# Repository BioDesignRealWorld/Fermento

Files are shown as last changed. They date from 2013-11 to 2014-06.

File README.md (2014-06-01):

Fermento
========

An open-source incubator for fun and profit. For more information about the project, see [biodesign.cc](http://biodesign.cc/2013/12/25/diy-incubator/).

Board
-----

* __Fab__ contains the PCB version to send to a professional PCB fabrication house. It has a nice silkscreen and slightly better component layout. 
* __Homebrew__ contains the version for homebrew PCB printing. The layout is one-sided for easier manufacturing. Drill plan and assembly instruction sheet included.
  To accomodate a single sided board, the wiring of the component to the microcontroller had to be changed. The correct pin mapping can be changed by a single line
  in the firmware.

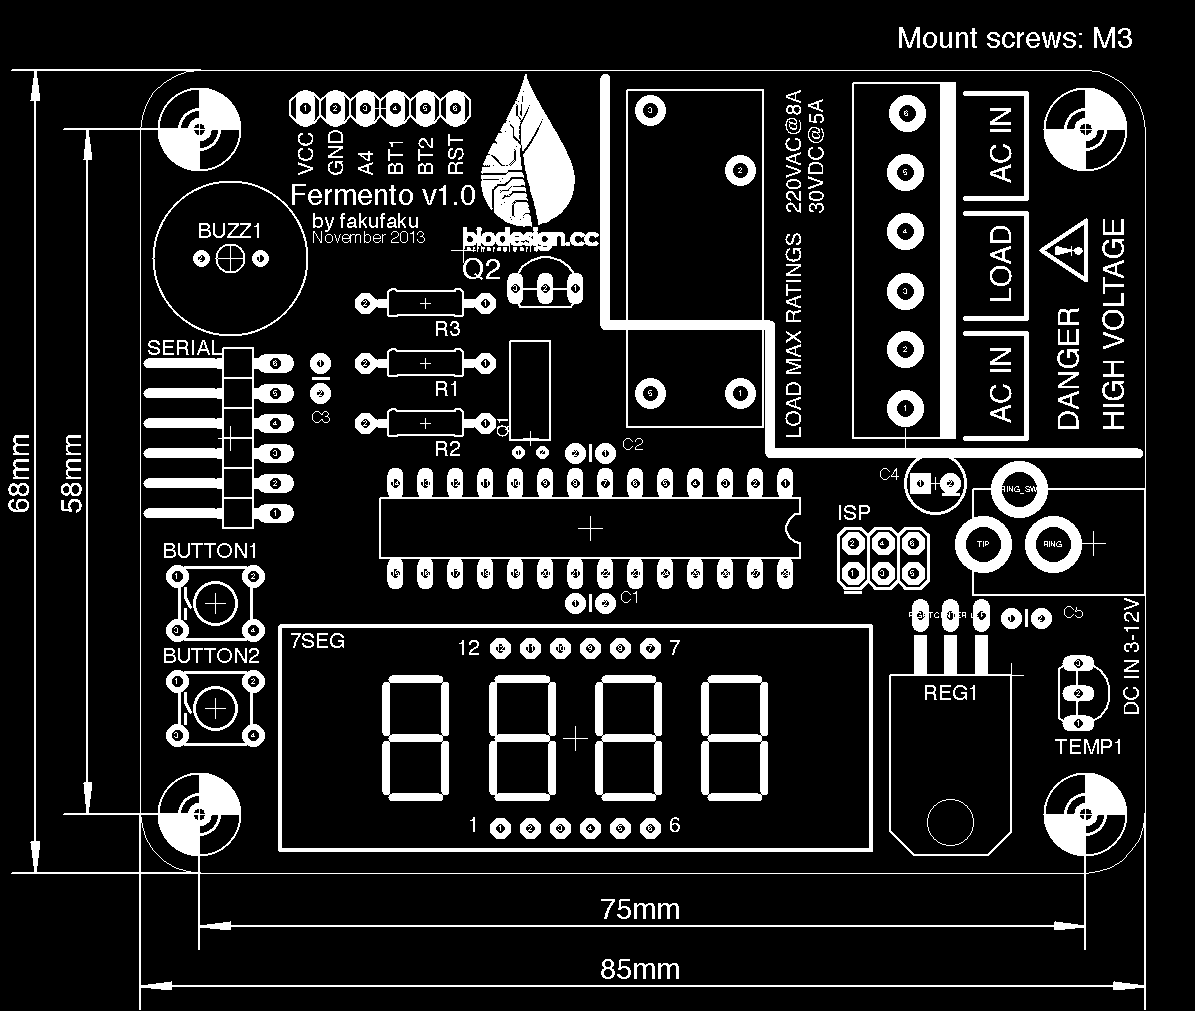
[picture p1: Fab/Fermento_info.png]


Bill Of Material
----------------

* 1x ATmega328p
* 1x DIP28 socket 
* 2x Tactile switch (through hole) (BUTTON1, BUTTON2) (C&K PTS645SM95-2 LFS)
* 2x Resistor 10K (R1, R3)
* 1x Resistor 1K (R2)
* 4x Capacitor 0.1uF, 2.5 mm pin spacing (C1, C2, C3, C5)
* 1x Electrolytic capacitor 47uF, radial, 2.5 mm pin spacing (C4)
* 1x 6-pin 90-degrees header (SERIAL)
* 1x 3x2-pin straight header (ISP)
* 1x 6-terminal screw block (Altech MBE-156)
* 1x Relay, 3VDC switching (Omron G6RL-1A-DC3)
* 1x 13mm buzzer (BUZZ1) (Murata, PKM13EPYH4000-A0)
* 1x DC jack 2.1mm (Kobiconn 163-179PH-EX)
* 1x 32.768kHz crystal (Q1) (ECS-.327-12.5-13X)
* 1x Mosfet transistor, TO92 (Q2) (Supertex TP2104N3-G)
* 1x 3.3V Regulator, TO220 (REG1) (TI TLV2217-33KCSE3)
* 1x Temperature sensor, TO92 (TEMP1) (TI LM61CIZ/NOPB)
* 1x 7-segment 4-digit display (7SEG) (Lumex LDQ-N514RI)

Wiring of the incubator
-----------------------

The board has a 6 pin terminal that allows minimal effort in wiring all the AC part of the circuit.

* The 2 wires from the bulb socket go into __LOAD__.
* The 2 wires from the plug go into one of the __AC IN__ terminal.
* The second __AC IN__ can be used to attach a female AC socket. This allows to connect there a DC outlet to power the board.

Power supply
------------

The board has a 2.1mm DC jack. The DC regulator requires an input of 3-12V DC.

Firmware
--------

To install the firmware in your Arduino IDE, do the following.

* Copy the folder `firmware/Fermento` to your local Arduino folder.
* Copy the content of `firmware/hardware` to local `Arduino/hardware`.
* Copy the content of `firmware/libraries` to local `Arduino/libraries`.

Then, chose `Tools -> Board -> ATmega328p on a breadboard`. Choose the sketch
`Fermento` from the sketchbook, and upload it.

In case you don't use the homebrew version, there is one line to comment out in
the sketch to change the pin mapping.

In the Fab version, an ISP header is provided to burn the bootloader. The Homebrew
version is lacking this, so a different board (such as the standard Arduino) needs
to be used to burn the bootloader. In addition, an ISP-programmer is needed.
An Arduino board can also be used to do [the job](http://arduino.cc/en/Tutorial/ArduinoISP).

Use it
------

Button1 and button2 control the incubation temperature and time respectively.

When button1 is shortly pressed the display switches to temperature. To set the
incubation temperature, keep button1 pressed until it displays the desired
temperature. The temperature regulation starts as soon as an incubation
temperatures different than 0 is set. Note that if the incubation temperature
is lower than room temperature, nothing happens.

When button2 is shortly pressed the display switches to incubation time
(hours:minutes). To set the incubation time, keep button2 pressed until the
desired incubation time is displayed. If you don’t set an incubation time, the
incubation will never stop. The time goes up in increments of 30 minutes.

Pressing button1 and button2 together for a few seconds resets incubation temperature and time to 0.

License
-------

2013 (c) Robin Scheibler, [CC BY-SA 3.0](https://creativecommons.org/licenses/by-sa/3.0/).

Based on [TokyoTime](http://robinscheibler.org/TokyoTime), itself based on SparkFun's [BigTime](https://www.sparkfun.com/products/11734).

The code uses the [Arduino PID library](http://playground.arduino.cc/Code/PIDLibrary).

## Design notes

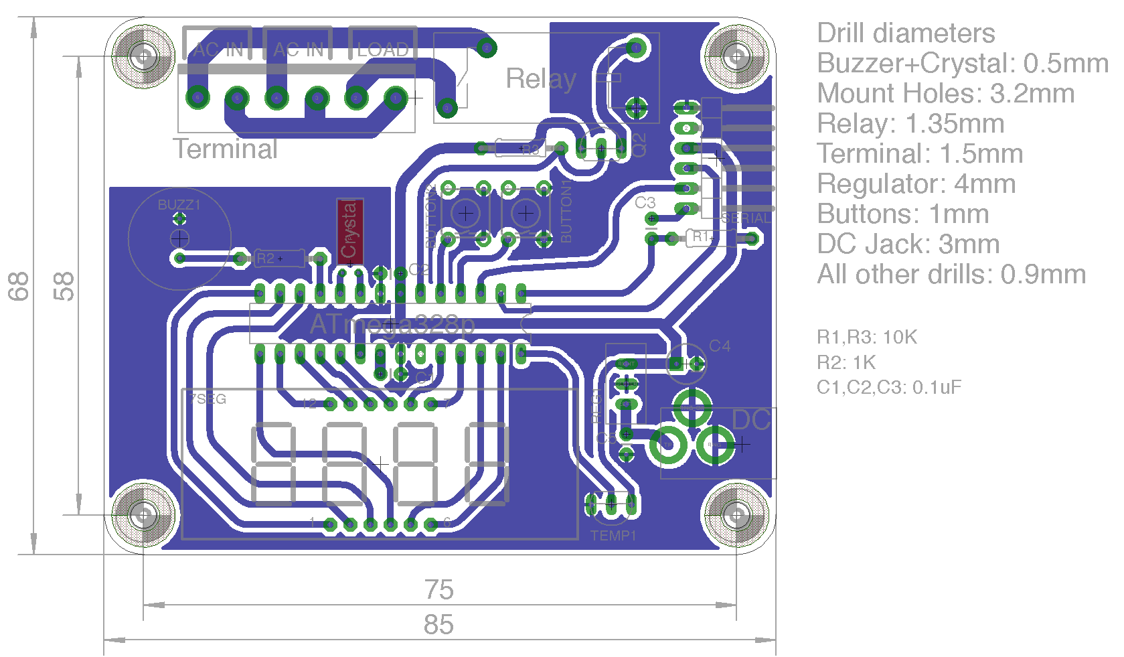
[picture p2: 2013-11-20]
Homebrew/Fermento_1side_brd.png

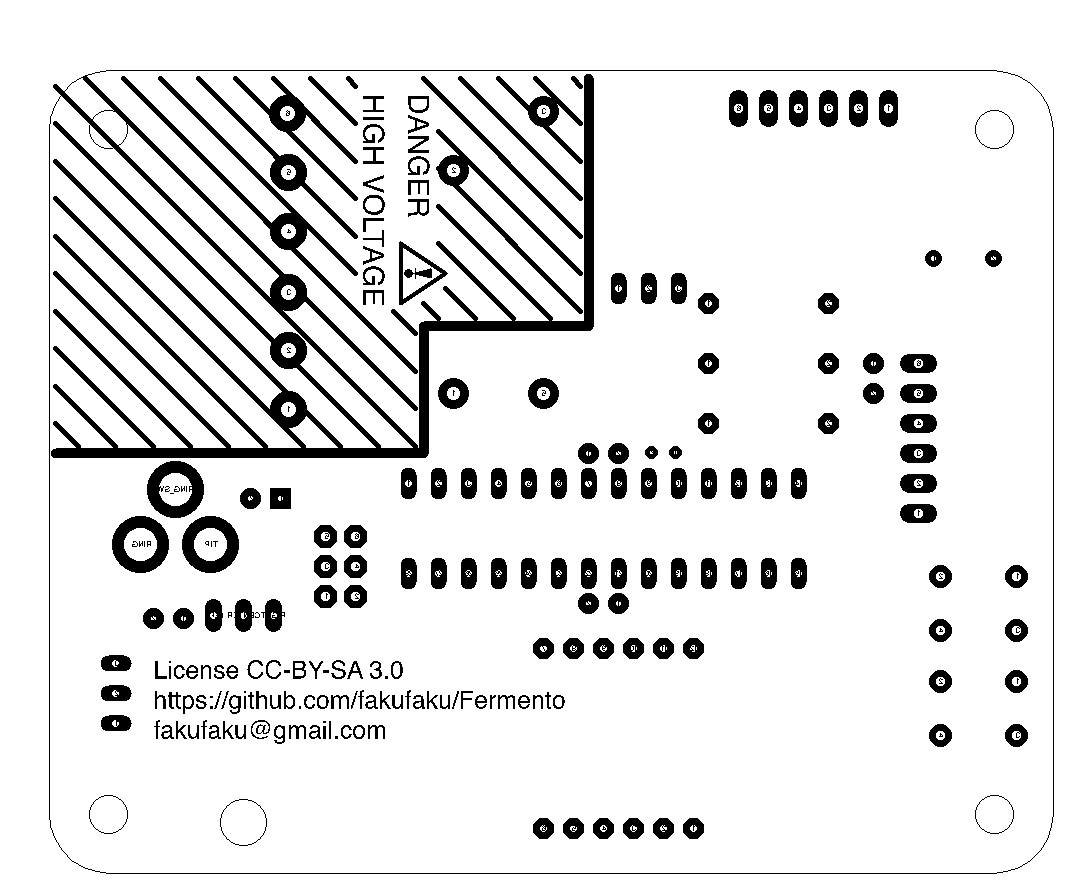
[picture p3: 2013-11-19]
Fab/Fermento_bot.png

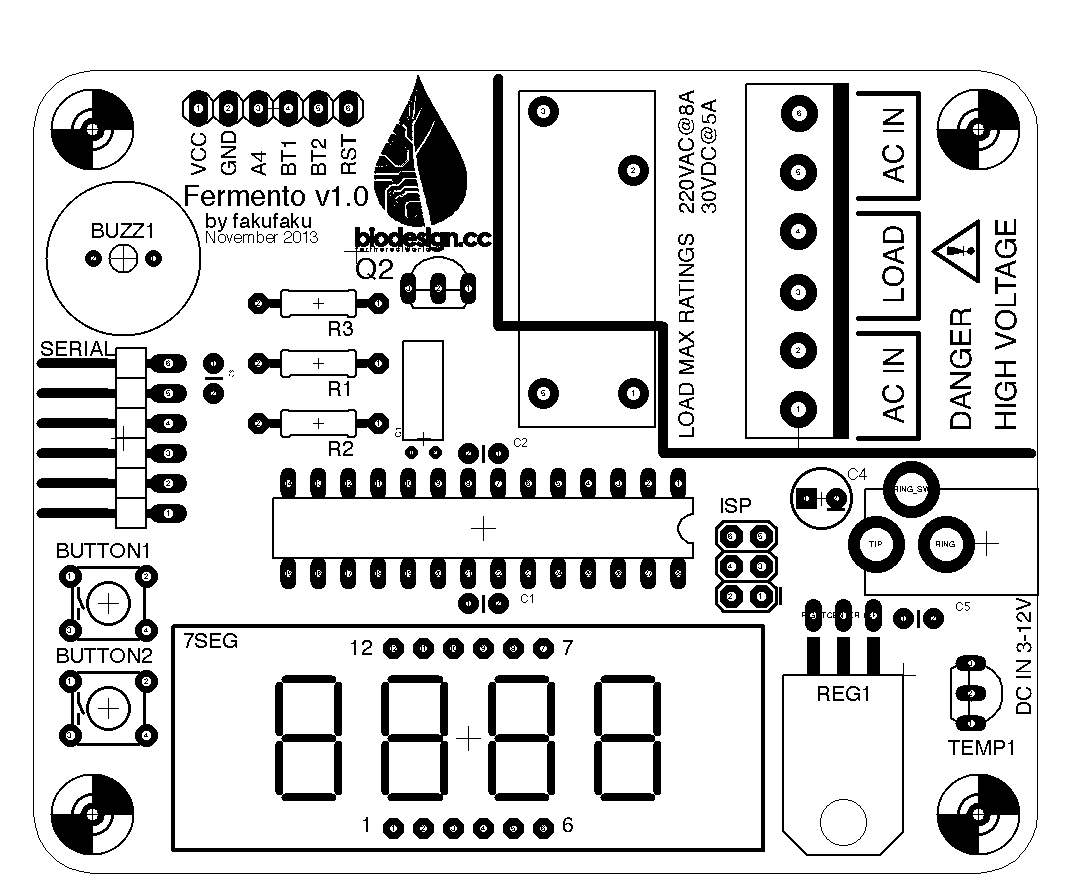
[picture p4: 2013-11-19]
Fab/Fermento_top.png

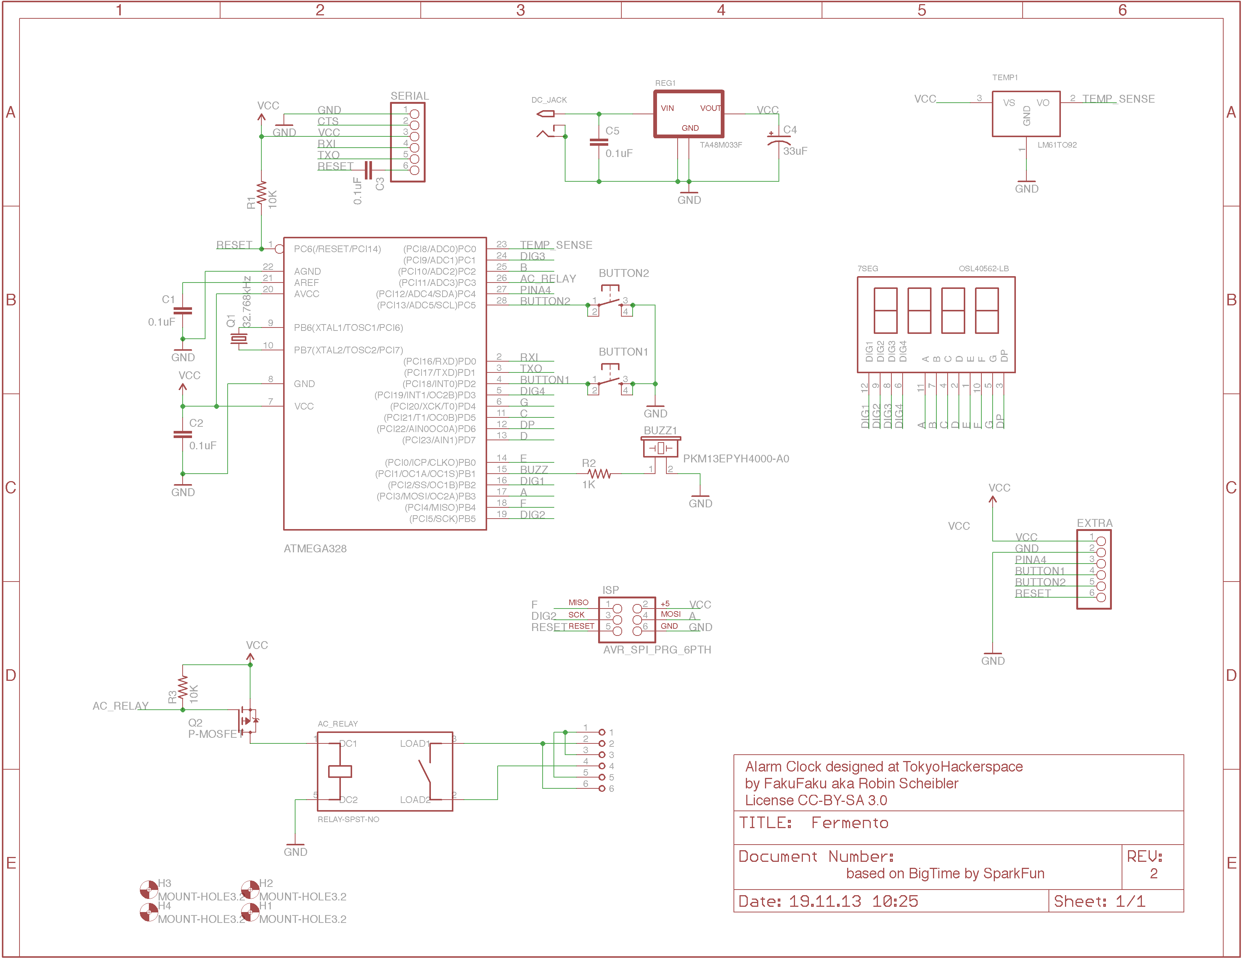
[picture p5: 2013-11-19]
Fab/Fermento_sch.png

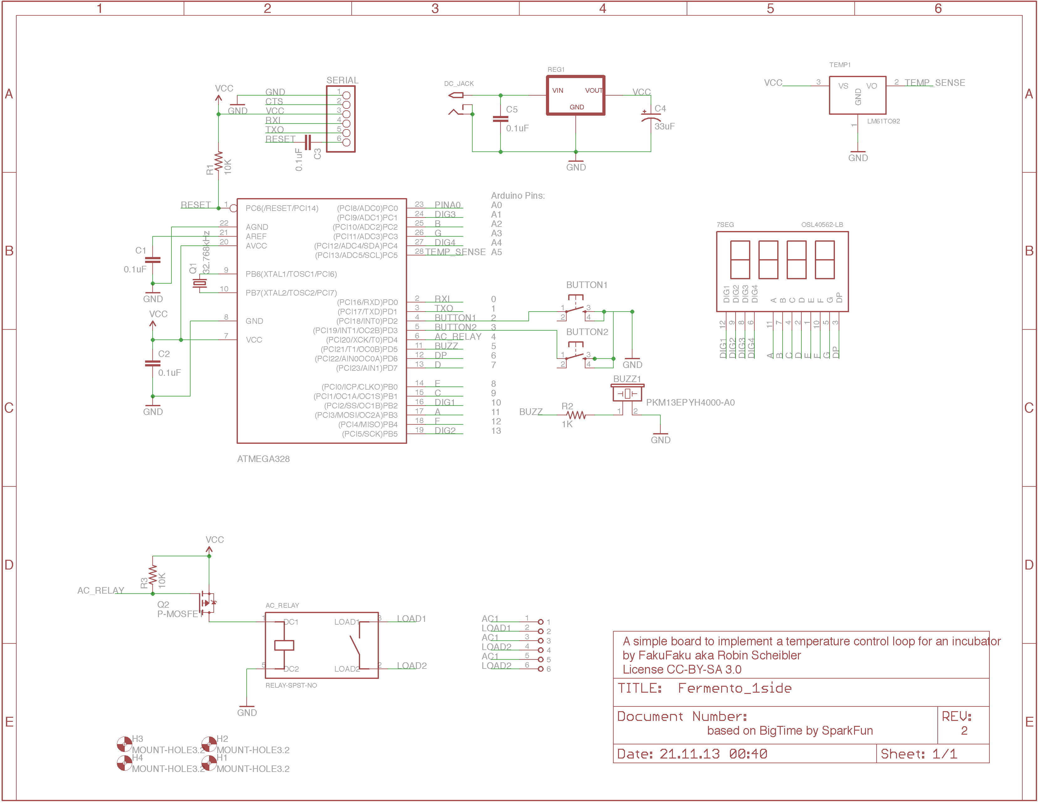
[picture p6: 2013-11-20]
Homebrew/Fermento_1side_sch.png

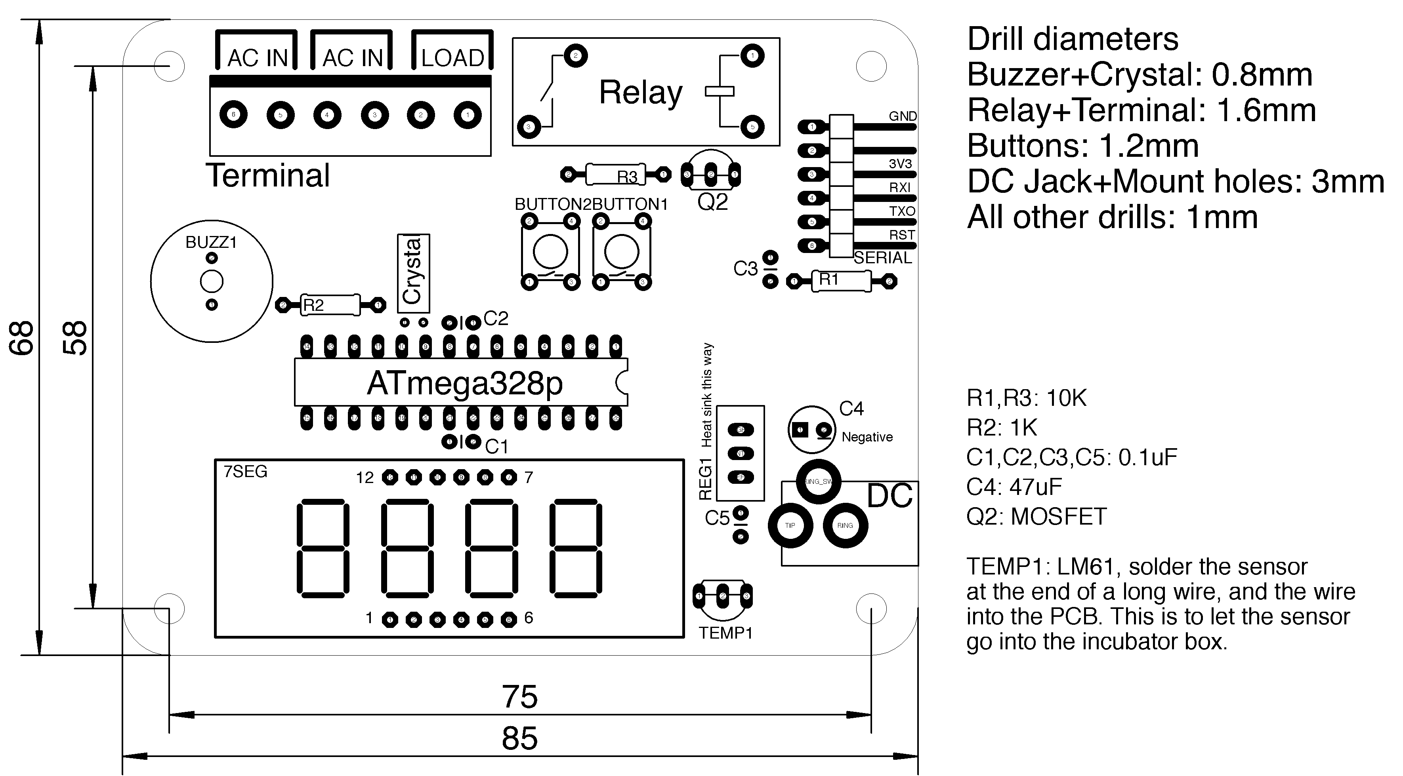
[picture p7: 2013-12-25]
Homebrew/Fermento_1side_info.png

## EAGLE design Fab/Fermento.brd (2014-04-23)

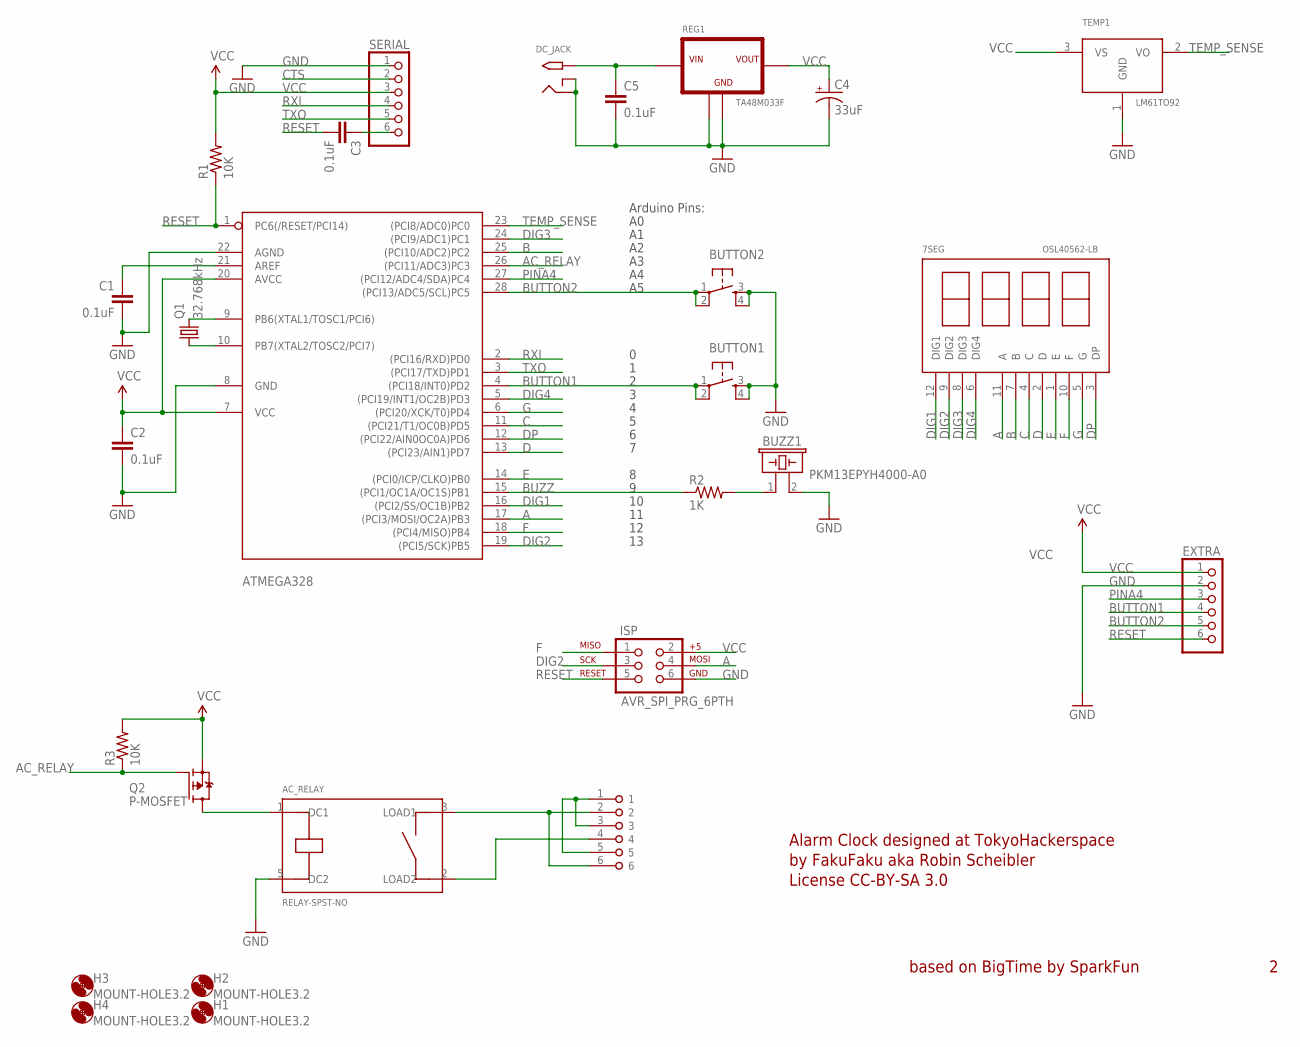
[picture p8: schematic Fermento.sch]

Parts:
7SEG: OSL40562-LB; OSL40562
AC_RELAY: RELAY-SPST-NO; G6RL-1A-DC3
ATMEGA328: ATMEGA168-20P; DIL28-3
BUTTON1, BUTTON2: TAC_SWITCHPTH; TACTILE-PTH
BUZZ1: PKM13EPYH4000-A0; PIEZO-MURATA-13MM
C1, C2, C3, C5: 0.1uF; CAP-PTH-SMALL
C4: 33uF; CPOL-RADIAL-10UF-25V
DC_JACK: 2.1MMJACKTHM; PJ-102A
EXTRA: PINHD-1X6; 1X06
H1, H2, H3, H4: MOUNT-HOLE3.2; 3,2
ISP: AVR_SPI_PRG_6PTH; 2X3
Q1: 32.768kHz; CRYSTAL-8X3-TH
Q2: P-MOSFET; TO92-
R1, R3: 10K; 0207/10
R2: 1K; 0207/10
REG1: TA48M033F; TO-220
SERIAL: PINHD-1X6/90; 1X06/90
TEMP1: LM61TO92; TO92-
U$2: TERMINAL-6; MBE-156

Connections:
A: 7SEG.11 (A), ATMEGA328.17 ((PCI3/MOSI/OC2A)PB3), ISP.4
AC_RELAY: ATMEGA328.26 ((PCI11/ADC3)PC3), Q2.2 (G), R3.1
AREF: ATMEGA328.21 (AREF), C1.1
B: 7SEG.7 (B), ATMEGA328.25 ((PCI10/ADC2)PC2)
BUTTON1: ATMEGA328.4 ((PCI18/INT0)PD2), BUTTON1.1, BUTTON1.2, EXTRA.4
BUTTON2: ATMEGA328.28 ((PCI13/ADC5/SCL)PC5), BUTTON2.1, BUTTON2.2, EXTRA.5
BUZZ: ATMEGA328.15 ((PCI1/OC1A/OC1S)PB1), R2.1
C: 7SEG.4 (C), ATMEGA328.11 ((PCI21/T1/OC0B)PD5)
CTS: SERIAL.2
D: 7SEG.2 (D), ATMEGA328.13 ((PCI23/AIN1)PD7)
DIG1: 7SEG.12 (DIG1), ATMEGA328.16 ((PCI2/SS/OC1B)PB2)
DIG2: 7SEG.9 (DIG2), ATMEGA328.19 ((PCI5/SCK)PB5), ISP.3
DIG3: 7SEG.8 (DIG3), ATMEGA328.24 ((PCI9/ADC1)PC1)
DIG4: 7SEG.6 (DIG4), ATMEGA328.5 ((PCI19/INT1/OC2B)PD3)
DP: 7SEG.3 (DP), ATMEGA328.12 ((PCI22/AIN0OC0A)PD6)
E: 7SEG.1 (E), ATMEGA328.14 ((PCI0/ICP/CLKO)PB0)
F: 7SEG.10 (F), ATMEGA328.18 ((PCI4/MISO)PB4), ISP.1
G: 7SEG.5 (G), ATMEGA328.6 ((PCI20/XCK/T0)PD4)
GND: AC_RELAY.5 (DC2), ATMEGA328.8 (GND), ATMEGA328.22 (AGND), BUTTON1.3, BUTTON1.4, BUTTON2.3, BUTTON2.4, BUZZ1.2, C1.2, C2.2, C4.2 (-), C5.2, DC_JACK.RING, DC_JACK.RING_SW, EXTRA.2, ISP.6, REG1.CENTER (GND), REG1.THERMAL (GND), SERIAL.1, TEMP1.1 (GND)
unnamed: ATMEGA328.9 (PB6(XTAL1/TOSC1/PCI6)), Q1.2
unnamed: ATMEGA328.10 (PB7(XTAL2/TOSC2/PCI7)), Q1.1
unnamed: C5.1, DC_JACK.TIP, REG1.LEFT (VIN)
unnamed: U$2.1, U$2.3, U$2.5
unnamed: AC_RELAY.3 (LOAD1), U$2.2, U$2.6
unnamed: C3.1, SERIAL.6
unnamed: AC_RELAY.2 (LOAD2), U$2.4
unnamed: BUZZ1.1, R2.2
PINA4: ATMEGA328.27 ((PCI12/ADC4/SDA)PC4), EXTRA.3
RELAY: AC_RELAY.1 (DC1), Q2.1 (D)
RESET: ATMEGA328.1 (PC6(/RESET/PCI14)), C3.2, EXTRA.6, ISP.5, R1.1
RXI: ATMEGA328.2 ((PCI16/RXD)PD0), SERIAL.4
TEMP_SENSE: ATMEGA328.23 ((PCI8/ADC0)PC0), TEMP1.2 (VO)
TXO: ATMEGA328.3 ((PCI17/TXD)PD1), SERIAL.5
VCC: ATMEGA328.7 (VCC), ATMEGA328.20 (AVCC), C2.1, C4.1 (+), EXTRA.1, ISP.2, Q2.3 (S), R1.2, R3.2, REG1.RIGHT (VOUT), SERIAL.3, TEMP1.3 (VS)

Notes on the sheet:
Alarm Clock designed at TokyoHackerspace
by FakuFaku aka Robin Scheibler
License CC-BY-SA 3.0
based on BigTime by SparkFun
Arduino Pins:

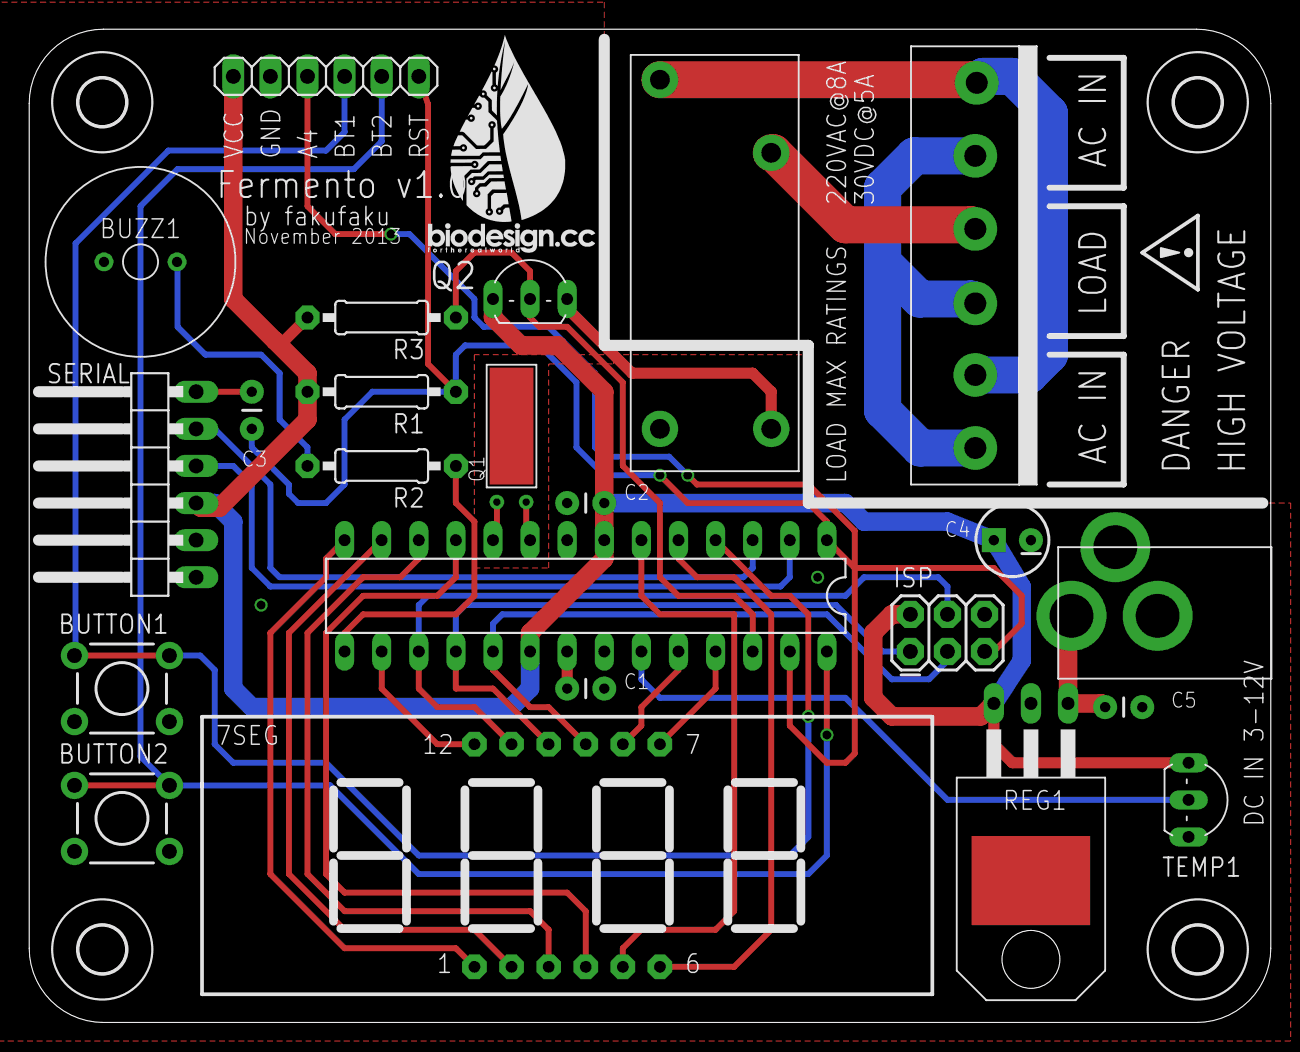
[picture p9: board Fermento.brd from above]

Board: 2 copper layers, 85.0 x 68.0 mm, 30 parts (1 on the bottom side), 33 nets.

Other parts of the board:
U$1, U$3: DANGER-SMALL
U$4: BIODESIGN-LOGO

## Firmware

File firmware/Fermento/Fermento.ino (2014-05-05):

/*
 * (c) Fakufaku 2013
 * This is the code for the homebrew incubator 'Fermento'
 * This code is released under the CC-BY-SA 3.0 License.
 * The part of the code that's used for the display on the 7-segment was ripped off the BigTime code from Nathan Seidl. I owe him a beer then.
 */

#include <math.h>

#include <PID_v1.h>

#define TRUE 1
#define FALSE 0

#define ENTER_CRIT()    {byte volatile saved_sreg = SREG; cli()
#define LEAVE_CRIT()    SREG = saved_sreg;}

//Careful messing with the system color, you can damage the display if
//you assign the wrong color. If you're in doubt, set it to red and load the code,
//then see what the color is.
#define RED  1
#define GREEN 2
#define BLUE  3
#define YELLOW  4
int systemColor = RED;
int display_brightness = 2000; //A larger number makes the display more dim. This is set correctly below.

// These define control how to turn on digits and segments
// Change these according to the type of seven-segment used (common anode/cathode)
// The default is set for common cathode
#define DIGIT_ON   LOW
#define DIGIT_OFF  HIGH
#define SEGMENT_ON  HIGH
#define SEGMENT_OFF LOW

// slow continuous PWM variables
#define PWM_MS 5000
#define PWM_MIN 100
#define RELAY_ON  LOW
#define RELAY_OFF HIGH

// PID loop parameter
#define PID_KP  50
#define PID_KI  1
#define PID_KD  1

// Some display related parameters (time in seconds, temperature in degrees Celsius)
#define TIME_INCREMENT 1800
#define MAX_TIME 356459
#define TEMP_INCREMENT 1
#define MAX_TEMP 65

//-=-=-=-=-=-=-=-=-=-=-=-=-=-=-=-=-=-=
// OPTIONS
//
// Voltage reference of the ADC
#define ADC_REF 3300
//
// Uncomment following line for the homebrew (1-sided) PCB version
//#define FERMENTO_1SIDE
//
// Uncomment the following line if you use the LM35 instead of the LM61 temperature sensor
//#define LM35
//-=-=-=-=-=-=-=-=-=-=-=-=-=-=-=-=-=-=

//-=-=-=-=-=-=-=-=-=-=-=-=-=-=-=-=-=-=
//Pin definitions
#ifdef FERMENTO_1SIDE
int digit1 = 10;    //Display pin 12
int digit2 = 13;    //Display pin 9
int digit3 = A1;    //Display pin 8
int digit4 = A4;     //Display pin 6

int segA = 11;      //Display pin 11
int segB = A2;      //Display pin 7
int segC = 9;       //Display pin 4
int segD = 7;       //Display pin 2
int segE = 8;       //Display pin 1
int segF = 12;      //Display pin 10
int segG = A3;       //Display pin 5

int colons = 6;     //Display pin 3

int temp_sen = A5;  // to read the temperature sensor

const static int buzz = 5;
const static int theButton = 2;
const static int theButton2 = 3;
const static int pwm_pin = 4;  // Pin 4

// The interrupt of button1 is on external interrupt 0
// The interrupt of button2 is on external interrupt 1
#define BUTTON1_INT_VECT INT0_vect
#define BUTTON2_INT_VECT INT1_vect
#define BUTTONS_INT_SET() do  \
  {                           \
    EICRA = (1<<ISC11) + (1<<ISC01); /* falling edge */ \
    EIMSK = (1<<INT1) + (1<<INT0);      \
  }                           \
  while (0)

#else

// Pin definition for the 2-layer PCB
int digit1 = 10;    //Display pin 12
int digit2 = 13;    //Display pin 9
int digit3 = A1;    //Display pin 8
int digit4 = 3;     //Display pin 6

int segA = 11;      //Display pin 11
int segB = A2;      //Display pin 7
int segC = 5;       //Display pin 4
int segD = 7;       //Display pin 2
int segE = 8;       //Display pin 1
int segF = 12;      //Display pin 10
int segG = 4;       //Display pin 5

int colons = 6;     //Display pin 3

int temp_sen = A0;  // to read the temperature sensor

const static int buzz = 9;
const static int theButton = 2;
const static int theButton2 = A5;
const static int pwm_pin = A3;  // Pin 4

// The interrupt of button1 is on external interrupt 0
// The interrupt of button2 is on PCINT13 (A5), on PCIE1.
#define BUTTON1_INT_VECT INT0_vect
#define BUTTON2_INT_VECT PCINT1_vect
#define BUTTONS_INT_SET() do  \
  {                           \
    EICRA = (1<<ISC01); /* falling edge */     \
    EIMSK = (1<<INT0);        \
    PCICR = (1 << PCIE1);     \
    PCMSK1 = (1 << PCINT13);  \
  }                           \
  while (0)

#endif
//-=-=-=-=-=-=-=-=-=-=-=-=-=-=-=-=-=-=


// Display status variable
#define TIME 1
#define TEMP 2
int display_status = TEMP;
int backoff = 0;  // just a short backoff for when we switch the display between TIME/TEMP
#define BACKOFFTIME 2
char disp_str[4];

// Variable to keep track of PWM window
unsigned long windowStartTime;

// control variables for PID
double t_incub;      // input to PID (temperature in incubator)
double t_incub_N;    // number of samples in t_incub average
double pwm_duty;     // output of PID
double t_set = 0;    // set point (target temperature)

//Specify the links and initial tuning parameters
PID myPID(&t_incub, &pwm_duty, &t_set, PID_KP, PID_KI, PID_KD, DIRECT);

// display timer (freeze parameters to display for 2 seconds)
int t_incub_disp;

// Timer variables
unsigned long timer_seconds = 0;

//The very important 32.686kHz interrupt handler
SIGNAL(TIMER2_OVF_vect)
{

  ENTER_CRIT();

  if (timer_seconds > 1)
  {
    timer_seconds--;
  }
  else if (timer_seconds == 1)
  {
    // reset timer
    timer_seconds = 0;
    // turn off by setting target temperature to zero
    t_set = 0;
    // Reset the PID
    myPID.SetMode(MANUAL);
    myPID.SetMode(AUTOMATIC);
  }

  // decrement backoff
  if (backoff > 0)
    backoff--;

  LEAVE_CRIT();
}

//The interrupt occurs when you push the button
SIGNAL(BUTTON1_INT_VECT)
{
  ENTER_CRIT();
  display_status = TEMP;
  backoff = BACKOFFTIME;
  LEAVE_CRIT();
}

SIGNAL(BUTTON2_INT_VECT)
{
  ENTER_CRIT();
  display_status = TIME;
  backoff = BACKOFFTIME;
  LEAVE_CRIT();
}

void setup()
{
  Serial.begin(57600);

  // set ADC reference to 3.3V
  analogReference(DEFAULT);

  // initialize pwm drive pin, and turn it off
  pinMode(pwm_pin, OUTPUT);
  digitalWrite(pwm_pin, HIGH);

  // initialize buzzer pin
  pinMode(buzz, OUTPUT);

  // initialize the buttons
  pinMode(theButton, INPUT);
  digitalWrite(theButton, HIGH); // pull-up
  pinMode(theButton2, INPUT);
  digitalWrite(theButton2, HIGH); // pull-up
  BUTTONS_INT_SET();

  //Setup TIMER2
  TCCR2A = 0x00;
  TCCR2B = (1<<CS22)|(1<<CS20); //Set CLK/128 or overflow interrupt every 1s
  ASSR   = (1<<AS2); //Enable asynchronous operation
  TIMSK2 = (1<<TOIE2); //Enable the timer 2 interrupt

  //These pins are used to control the display
  pinMode(segA, OUTPUT);
  pinMode(segB, OUTPUT);
  pinMode(segC, OUTPUT);
  pinMode(segD, OUTPUT);
  pinMode(segE, OUTPUT);
  pinMode(segF, OUTPUT);
  pinMode(segG, OUTPUT);

  pinMode(digit1, OUTPUT);
  pinMode(digit2, OUTPUT);
  pinMode(digit3, OUTPUT);
  pinMode(digit4, OUTPUT);
  pinMode(colons, OUTPUT);

  // setup PID stuff
  myPID.SetOutputLimits(PWM_MIN-1, PWM_MS-PWM_MIN+1);
  myPID.SetMode(AUTOMATIC);
  myPID.SetSampleTime(PWM_MS);
  windowStartTime = millis();

  // initialize pwm
  pwm_duty = 0; // off
  t_incub = read_temperature();
  t_incub_N = 1;

  // initialize slow variables for display
  t_incub_disp = t_incub;

}

void loop()
{
  
  temperatureControl();

  // display and output to serial
  if (display_status == TEMP)
  {
    displayTemperature((int)(t_incub_disp), FALSE); //Each call takes about 8ms, display the colon
  }
  else
  {
    unsigned int timer_disp;
    if (timer_seconds % 60 != 0)
      timer_disp = seconds2hours_minutes(timer_seconds + (60 - (timer_seconds%60)));
    else
      timer_disp = seconds2hours_minutes(timer_seconds);
    displayTime(timer_disp, TRUE); //Each call takes about 8ms, display the colon 
  }

  // handle buttons
  int b1 = digitalRead(theButton);
  int b2 = digitalRead(theButton2);

  if (b1 == LOW && b2 == LOW)
  {
    delay(10);
    if (backoff == 0)
    {
      // system reset
      timer_seconds = 0;
      t_set = 0;
      // reset PID
      myPID.SetMode(MANUAL);
      myPID.SetMode(AUTOMATIC);
    }
  }
  else if (b1 == LOW)
  {
    delay(10);
    if (backoff == 0)
      setTemperature();
  }
  else if (b2 == LOW)
  {
    delay(10);
    if (backoff == 0)
      setTime();
  }

}

// Simple PWM based on millis directly
void temperatureControl()
{
  unsigned long now = millis();

  // averaging over the whole 5 seconds
  t_incub += (read_temperature() - t_incub)/(++t_incub_N);

  if(now - windowStartTime > PWM_MS)
  { 
    // compute new pwm value for that window
    if (t_set != 0)
      myPID.Compute();

    // start a new relay window
    windowStartTime = now;

    // restart averaging of temperature
    t_incub_disp = t_incub;
    t_incub = read_temperature();
    t_incub_N = 1;

  }

  // if t_set is zero, that means incubator is off
  if (t_set < 1)
  {
    pwm_duty = 0;
  }

  // control the slow PWM
  if (pwm_duty < PWM_MIN)
  {
    digitalWrite(pwm_pin, RELAY_OFF);
  }
  else if (pwm_duty < PWM_MS-PWM_MIN)
  {
    if(pwm_duty > now - windowStartTime) 
      digitalWrite(pwm_pin, RELAY_ON);
    else 
      digitalWrite(pwm_pin, RELAY_OFF);
  }
  else
  {
    digitalWrite(pwm_pin, RELAY_ON);
  }
}

float read_temperature()
{
  // make an average of 10 readings of the ADC
  float A = 0;
  for (int i=0 ; i < 10 ; i++)
    A += analogRead(temp_sen);
  A /= 10;

  // convert the ADC output to a temperature
#ifndef LM35
  // LM61 sensor
  return (A/1023.*ADC_REF - 600)/10;
#else
  // LM35 sensor
  return (A/1023.*ADC_REF)/10;
#endif
}

//This routine occurs when you hold the button 1 down
//The colon blinks indicating we are in this mode
//Holding the button down will increase the time (accelerates)
//Releasing the button for more than 2 seconds will exit this mode
void setTemperature()
{
  ENTER_CRIT();

  int idleMiliseconds = 0;
  //This is the timeout counter. Once we get to ~2 seconds of inactivity, the watch
  //will exit the setTemperature function and return to normal operation

  while(idleMiliseconds < 2000) {

    for(int x = 0 ; x < 10 ; x++) {
      displayTemperature(t_set, TRUE); //Each call takes about 8ms, display the colon for about 100ms
      delayMicroseconds(display_brightness); //Wait before we paint the display again
    }
    for(int x = 0 ; x < 10 ; x++) {
      displayTemperature(t_set, FALSE); //Each call takes about 8ms, turn off the colon for about 100ms
      delayMicroseconds(display_brightness); //Wait before we paint the display again
    }

    //If you're still hitting the button, then increase the time and reset the idleMili timeout variable
    if(digitalRead(theButton) == LOW) {
      idleMiliseconds = 0;

      t_set = ((int)(t_set+TEMP_INCREMENT) % MAX_TEMP); // Increase temperature
    }

    idleMiliseconds += 200;
  }

  LEAVE_CRIT();
}

//This routine occurs when you hold the button 2 down
//The colon blinks indicating we are in this mode
//Holding the button down will increase the time (accelerates)
//Releasing the button for more than 2 seconds will exit this mode
void setTime()
{
  ENTER_CRIT();
  
  // restart timer
  timer_seconds = 0;

  int idleMiliseconds = 0;
  //This is the timeout counter. Once we get to ~2 seconds of inactivity, the watch
  //will exit the setTime function and return to normal operation

  while(idleMiliseconds < 2000) 
  {

    unsigned int timer_disp = seconds2hours_minutes(timer_seconds);

    for(int x = 0 ; x < 10 ; x++) {
      displayTime(timer_disp, TRUE); //Each call takes about 8ms, display the colon for about 100ms
      delayMicroseconds(display_brightness); //Wait before we paint the display again
    }
    for(int x = 0 ; x < 10 ; x++) {
      displayTime(timer_disp, FALSE); //Each call takes about 8ms, turn off the colon for about 100ms
      delayMicroseconds(display_brightness); //Wait before we paint the display again
    }

    //If you're still hitting the button, then increase the time and reset the idleMili timeout variable
    if(digitalRead(theButton2) == LOW) {
      idleMiliseconds = 0;

      timer_seconds = ((timer_seconds+TIME_INCREMENT) % MAX_TIME); // Increase timer
    }

    idleMiliseconds += 200;
  }
  LEAVE_CRIT();
}
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

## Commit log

2013-11-19 Initial commit.
    [Fermento.brd, Fermento.sch]
2013-11-19 Added the one-sided version.
    [Fermento.brd, Fermento_1side.brd, Fermento_1side.sch]
2013-11-19 Added 1 sided version and png images.
    [Fermento_1side.brd, Fermento_1side.sch]
2013-11-20 Added mask and info diagram for 1sided homebrew incubator.
    [Fermento.brd, Fermento_1side.brd, Fermento_1side.sch]
2013-11-20 board difference added to README.
2013-11-20 One sided homebrew-friendly design redone.
    [Fermento_1side.brd, Fermento_1side.sch]
2013-11-27 Added firmware to the repo.
    [Fermento.sch, Fermento_1side.brd]
2013-11-27 Added fermento arduino sketch.
2013-12-25 Cleaned up for biodesign.cc post.
    [Fermento.GBL, Fermento.GBO, Fermento.GBS, Fermento.GTL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]
2014-01-10 Added the mask file for homebrew pcb.
2014-04-23 Fixed name of microcontroller in README and boards.txt file.
2014-04-23 Added kindof datasheet for Fab board.
    [Fermento.brd]
2014-05-02 Remove a wrong pin pushed by mistake to the repo. Added an option to use LM35 sensor and an option for easily changing the ADC voltage repference.
2014-06-01 Added ATmega328p to bill of material (duh).
